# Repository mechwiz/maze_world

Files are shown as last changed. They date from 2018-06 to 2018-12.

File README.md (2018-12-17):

# Effect of Planning Depth in Predator-Prey Behavior
**Michael Wiznitzer**

Northwestern University: Final Project

## Introduction
Nature is a wonder of its own. When we look at animals, we usually see cute furry creatures that seemingly just do their own thing. After seeing them in the wild, though, you begin to notice how they use their environment to hunt or hide from other animals. For [example](https://youtu.be/LhSDxp0oQK8?t=2m51s), a leapord might hide in a narrow valley as it hunts imapla grazing above it. In order to better understand these predator-prey relationships, [research](https://nxr.northwestern.edu/planning-vertebrates) has been done in the NxR lab to simulate how prey will act (using POMDPs) given various planning depths in order to reach some goal position before a predator kills the prey. My project focuses on turning these simulations into a 3-D honeycomb-styled-world realization where Sphero robots act as the predator and prey that have to navigate in various levels of occluded environments.

####  Objective
The goal of this project is to demonstrate the effect of planning-depth in regards to prey being able to reach some goal position before the predator kills it in a 3-D honeycomb-styled-world environment with various levels of occlusion. This project breaks down into 3 different parts listed below:

- Maze Fabrication
- Sphero Control with ROS
- Image Processing to determine robot location in maze

To read more about each part, see my portfolio post [here](https://mechwiz.github.io/Portfolio/prey.html). This repo's purpose is to highlight all of the differenct modules designed and created for the **Maze Fabrication** part above. To read more about how to setup the sphero control package, see my other repo [here](https://github.com/mechwiz/maze_control).

## Maze Fabrication
There are two parts to designing the maze within which the 3-D simulations will occur. The obvious part is designing the full-scale maze which looks something like the picture below based on the specs described in my portfolio post.

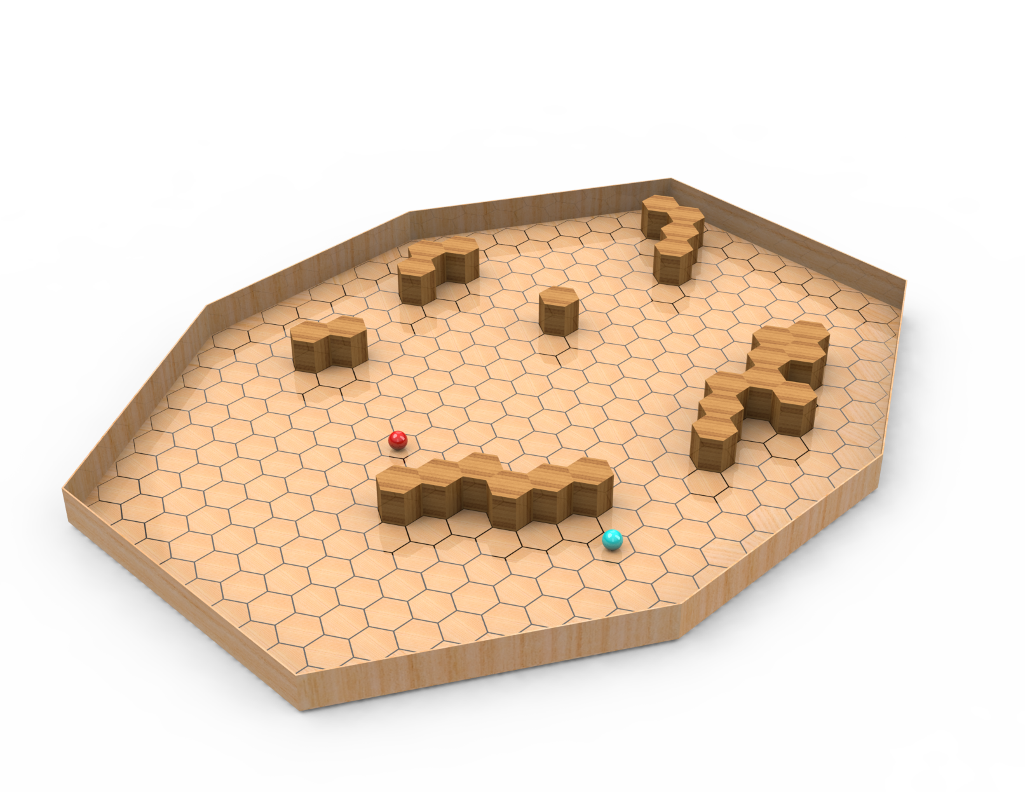
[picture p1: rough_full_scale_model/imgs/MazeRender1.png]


The full-scale maze includes 349 hexagonal cells and is roughly 8ft long by 6.25ft wide by 0.5ft tall. Due to the large size of the maze, the pieces are modular so that assembly and takedown is relatively straightforward.

Before building the full-scale maze, a small-scale version was made so that testing with the other parts of the project (i.e. controlling the Sphero robots with ROS via Image Processing) could be done. This way, if any modificaitons to the small scale maze had to be done in the interest of the other parts, they could be incorporated into the full-scale maze design. These changes are discussed in the **Full Scale Maze Design** section.

### Small Scale Maze Design
The small-scale maze design assembly model and actual laser-cut model are shown side by side below:

CAD Model                                                                          | Laser-cut Model
:---------------------------------------------------------------------------------:|:---------------------------------------------------------------------------------:
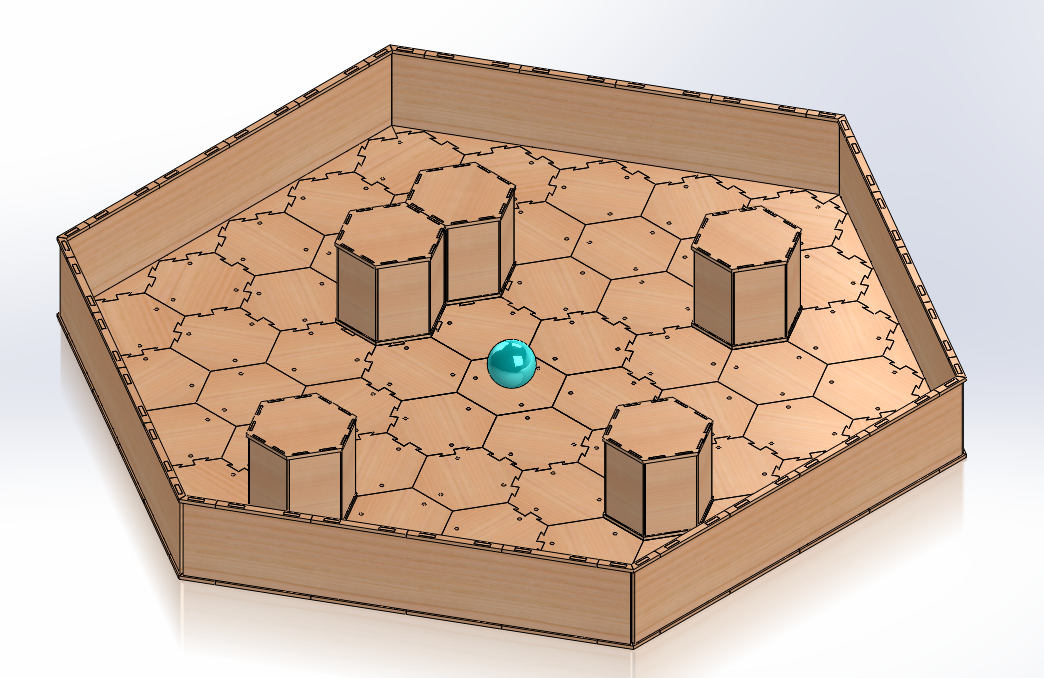
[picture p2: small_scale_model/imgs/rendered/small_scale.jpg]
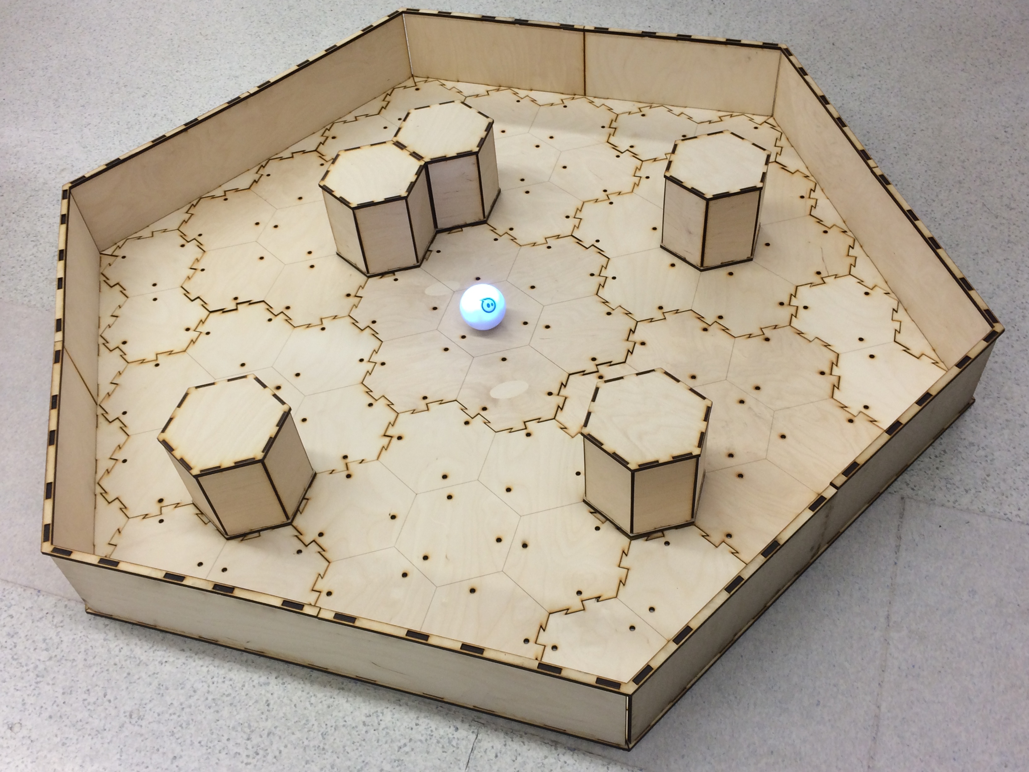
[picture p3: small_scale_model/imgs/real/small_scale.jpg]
 | 

The module pieces incorporated are described in the table below.

Description| CAD Model                                                                           | Laser-cut Model
:----------|:----------------------------------------------------------------------------------:|:----------------------------------------------------------------------------------:
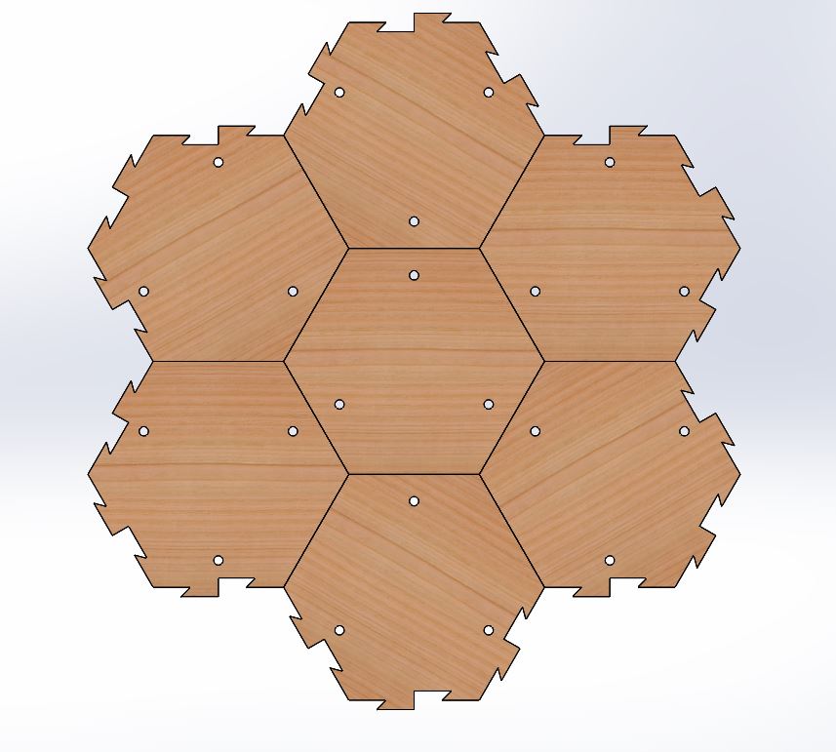
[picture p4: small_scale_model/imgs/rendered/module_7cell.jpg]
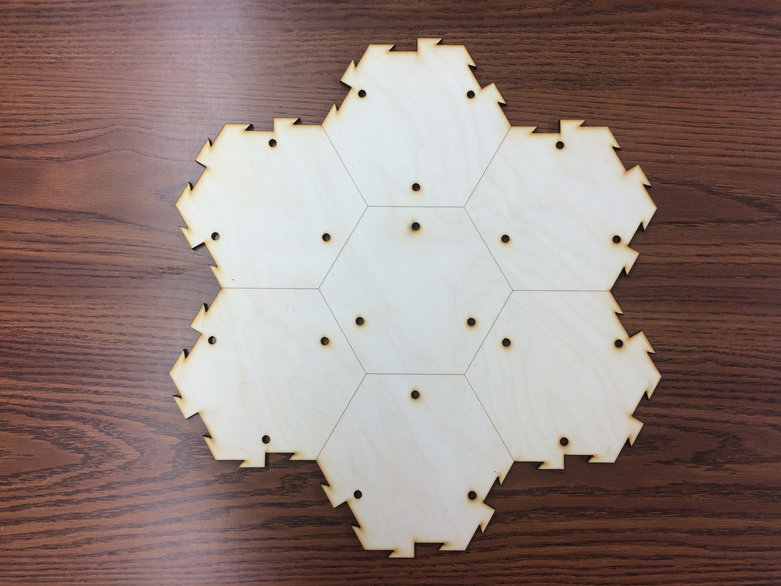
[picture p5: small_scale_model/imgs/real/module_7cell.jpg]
Modular interlocking floor piece with 7 cells <br /> (holes allow for obstacles to be "plugged" into the board via dowel pins) <ul><li>[DXF Files](small_scale_model/modules/module_7cell/dxf)</li><li>[SVG Files](small_scale_model/modules/module_7cell/svg)</li></ul> <br /> _7 modules_ |  | 
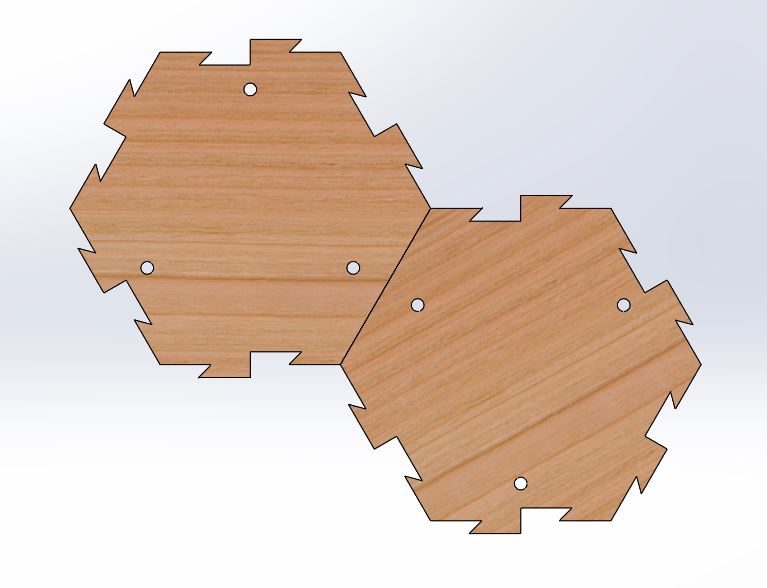
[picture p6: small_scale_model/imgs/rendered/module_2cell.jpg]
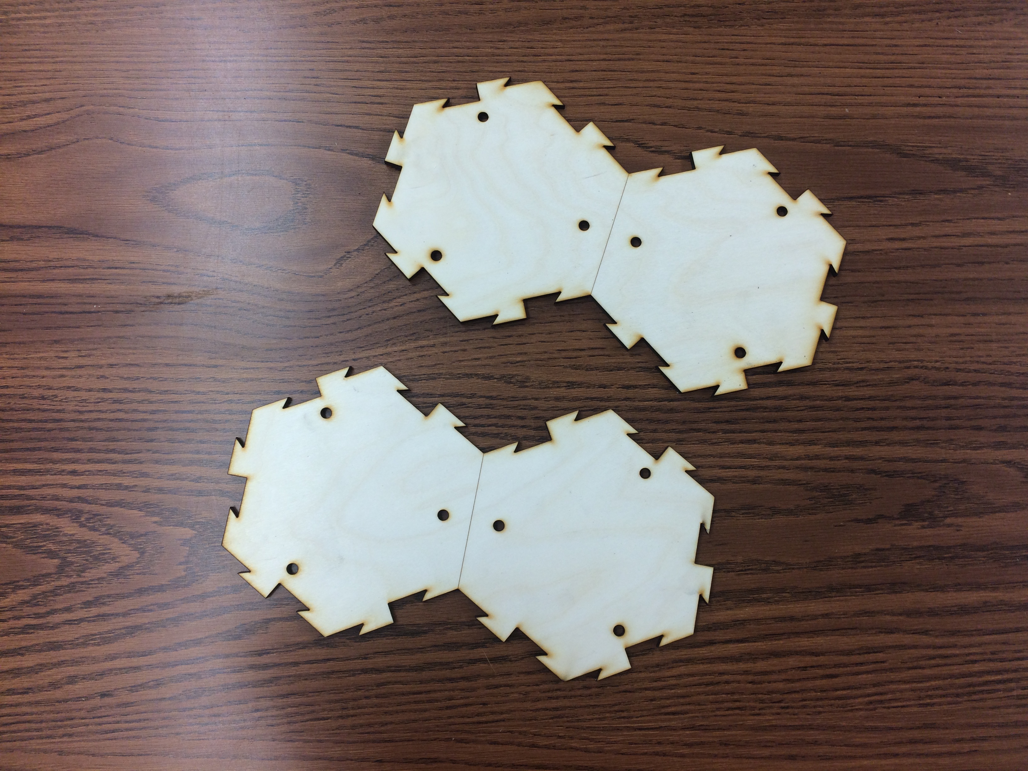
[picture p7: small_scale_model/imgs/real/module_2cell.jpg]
Modular interlocking floor piece with 2 cells <br /> (holes allow for obstacles to be "plugged" into the board via dowel pins) <ul><li>[DXF Files](small_scale_model/modules/module_2cell/dxf)</li><li>[SVG Files](small_scale_model/modules/module_2cell/svg)</li></ul> <br /> _4 modules_ |  | 
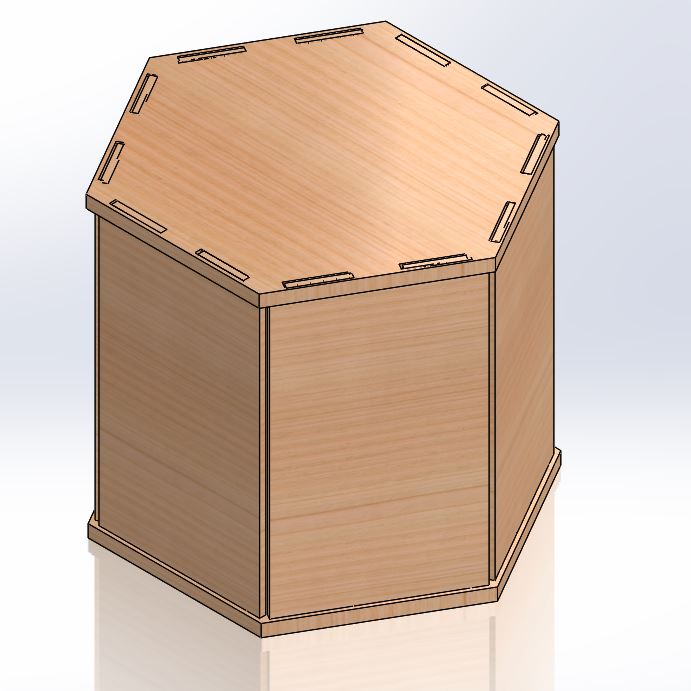
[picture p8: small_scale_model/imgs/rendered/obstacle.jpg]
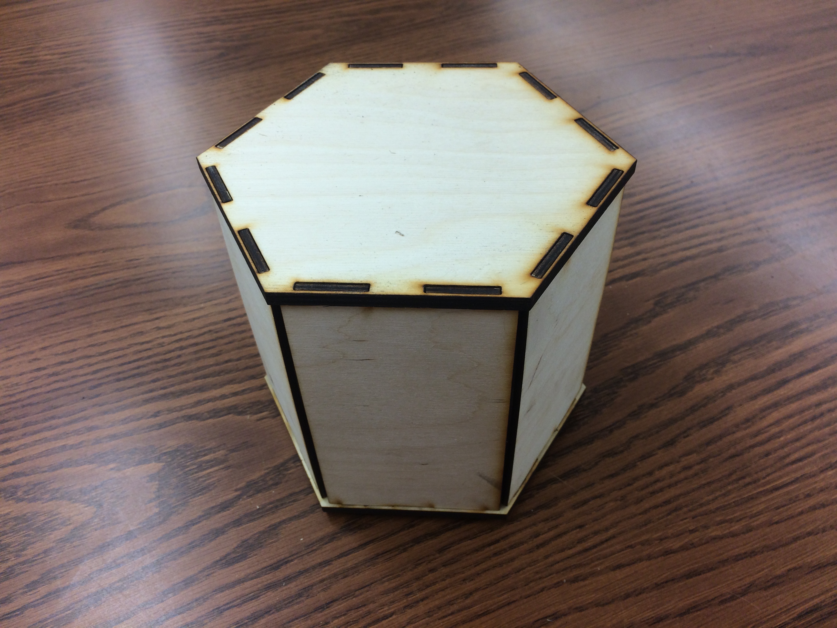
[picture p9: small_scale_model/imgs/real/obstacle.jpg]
Obstacle for blocking path of Sphero <br /> (uses a press-fit design; dowel pins glued <br /> on bottom are aligned with holes on the board) <ul><li>[DXF Files](small_scale_model/modules/obstacles/dxf)</li><li>[SVG Files](small_scale_model/modules/obstacles/svg)</li></ul> <br /> _Number of modules can vary_ |      | 
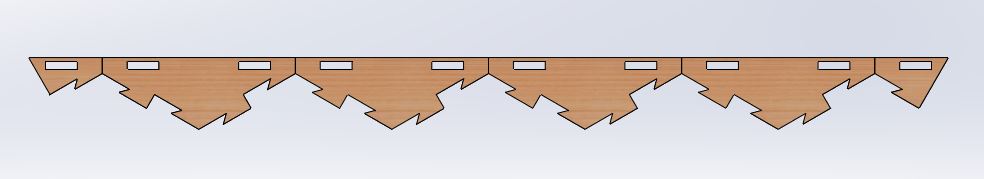
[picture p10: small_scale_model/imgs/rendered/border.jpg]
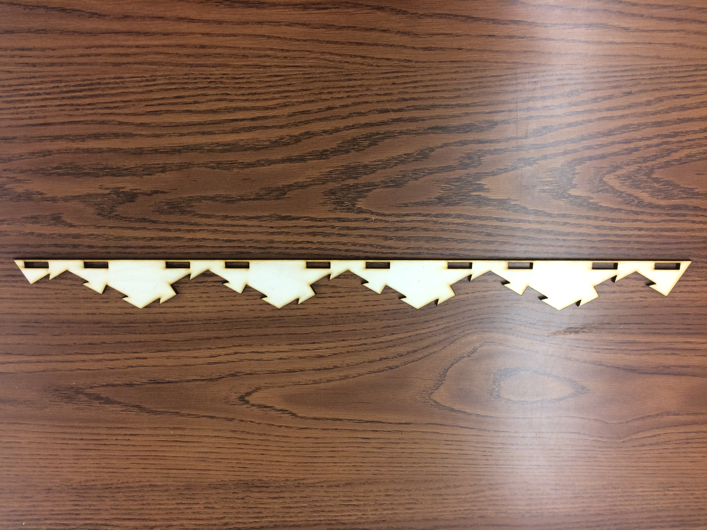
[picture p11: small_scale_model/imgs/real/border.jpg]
Interlocking border piece with the floor and wall pieces <ul><li>[DXF Files](small_scale_model/modules/border/dxf)</li><li>[SVG Files](small_scale_model/modules/border/svg)</li></ul> <br /> _6 modules_ |        | 
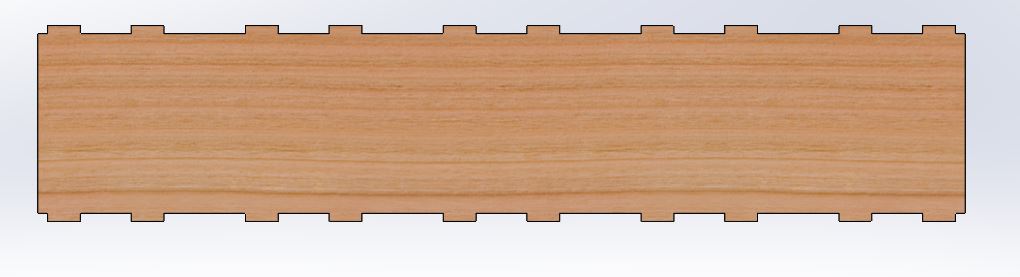
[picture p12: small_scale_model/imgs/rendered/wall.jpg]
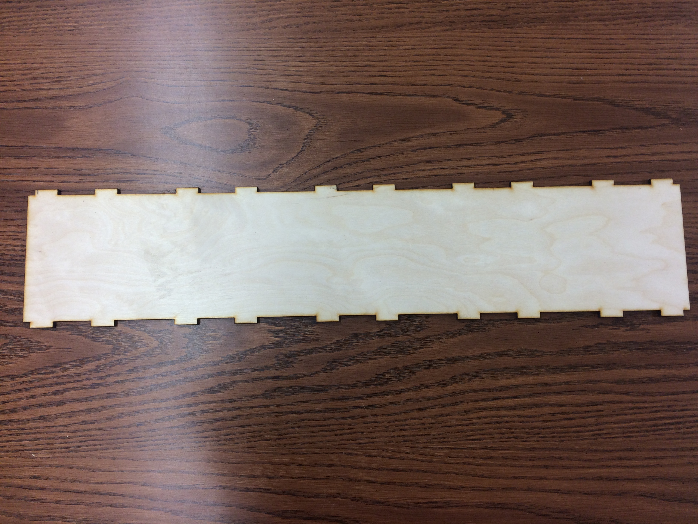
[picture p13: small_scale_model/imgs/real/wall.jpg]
Modular wall that fits into the border pieces <ul><li>[DXF Files](small_scale_model/modules/walls/dxf)</li><li>[SVG Files](small_scale_model/modules/walls/svg)</li></ul> <br /> _6 modules_ |          | 
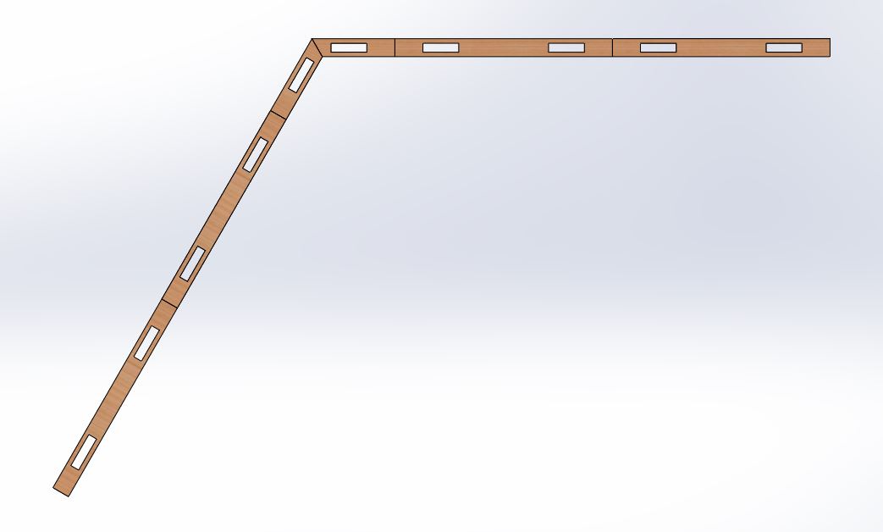
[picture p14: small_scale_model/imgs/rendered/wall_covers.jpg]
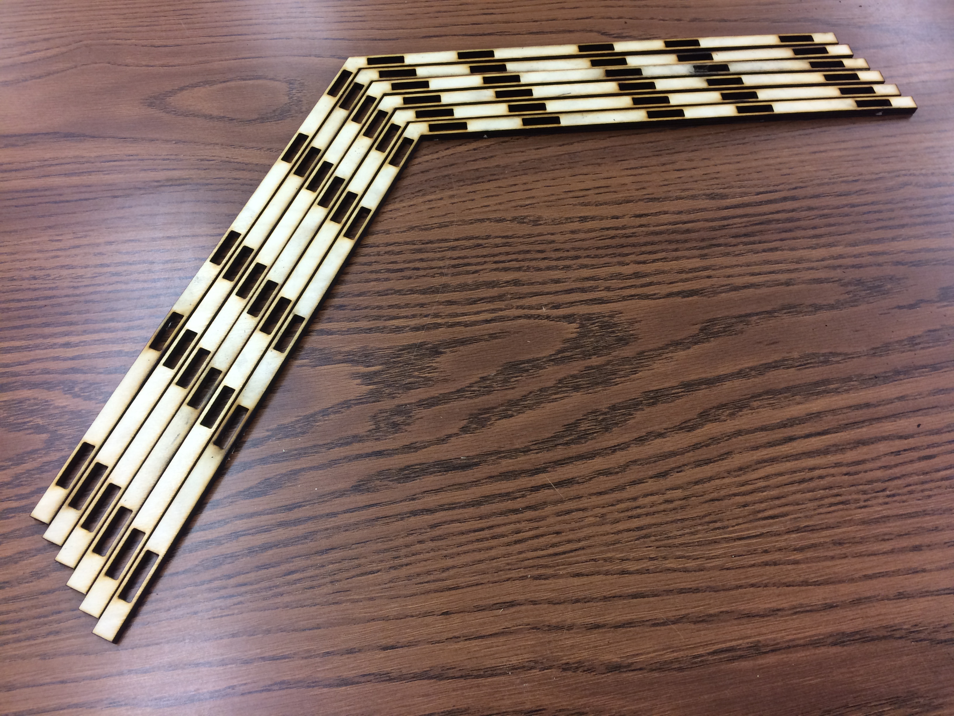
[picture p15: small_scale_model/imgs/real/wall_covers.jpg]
Modular wall cover that secures the wall pieces together <ul><li>[DXF Files](small_scale_model/modules/wall_covers/dxf)</li><li>[SVG Files](small_scale_model/modules/wall_covers/svg)</li></ul> <br /> _6 modules_ |   | 

### Full Scale Maze Design
The current full-scale maze design assembly model is shown below. Some modifications were made based on testing in the small-scale maze and due to size restrictions. There was no space available that could fit the maze with its original dimensions (11ft long by 8.6ft wide) so the cell size was reduced (where each side of the hexagon was changed from 3.5in to 2.5in) in order to maintain the same number of cells as required by spec. As such, the Sphero 2.0 was no longer an option as its diameter is roughly 3 inches. The Sphero Mini was chosen instead as its diameter is a little under 2 inches. Hence all full-scale module pieces were modified to reflect this change. The other change that will be implemented based on testing in the small-scale and full-scale mazes is that a [clear vinyl mat](https://www.marinevinylfabric.com/products/clear-marine-vinyl?variant=14023793573972) will be spread out over the surface of the maze. This is because some of the wood pieces are slightly warped which makes some catch points near the module connections that could potentially inhibit movement of the Sphero Mini (something that wasn't an issue for the Sphero 2.0). The mat will help make a continous smooth surface that the Sphero Mini will be able to move on with no issue. It should also be noted that holes will be punched on the mat corresponding to the hole places on the wood surface of the maze. These holes will not inhibit the Sphero movement as the mat is very thin (around 0.4 mm). Also note that because each cell of the maze will be labeled using a labeling scheme, the holes will always line up with those on the mat.

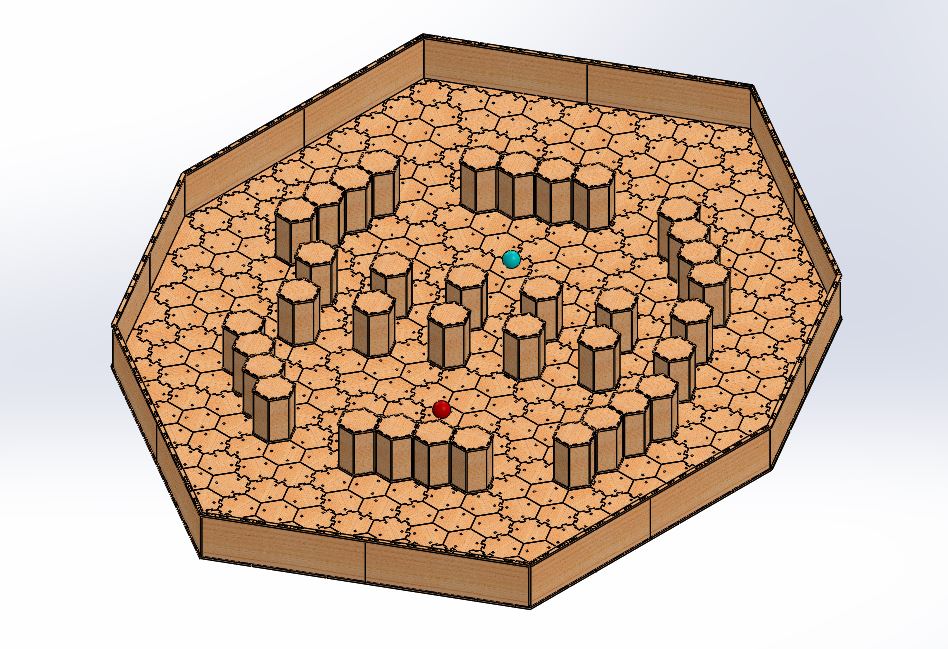
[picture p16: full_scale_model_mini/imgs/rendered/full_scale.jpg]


The module pieces incorporated are described in the table below.

Description| CAD Model                                                                           | Laser-cut Model
:----------|:----------------------------------------------------------------------------------:|:----------------------------------------------------------------------------------:
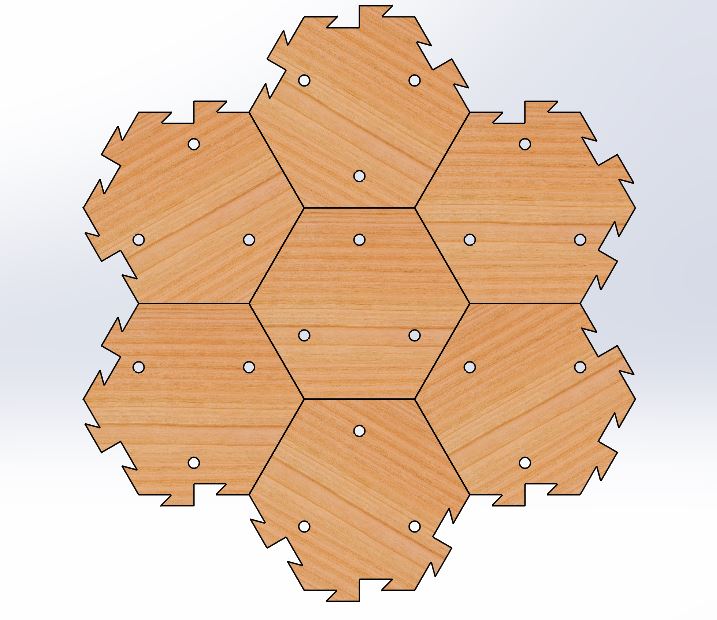
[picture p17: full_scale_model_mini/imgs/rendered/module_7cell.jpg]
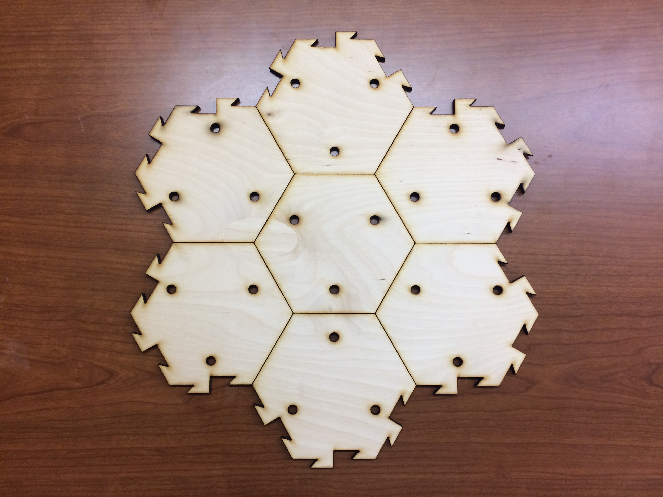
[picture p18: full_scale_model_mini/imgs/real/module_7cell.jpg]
Modular interlocking floor piece with 7 cells <br /> (holes allow for obstacles to be "plugged" into the board via dowel pins) <ul><li>[DXF Files](full_scale_model_mini/modules/module_7cell/dxf)</li><li>[SVG Files](full_scale_model_mini/modules/module_7cell/svg)</li></ul> <br /> _41 modules_ |  | 
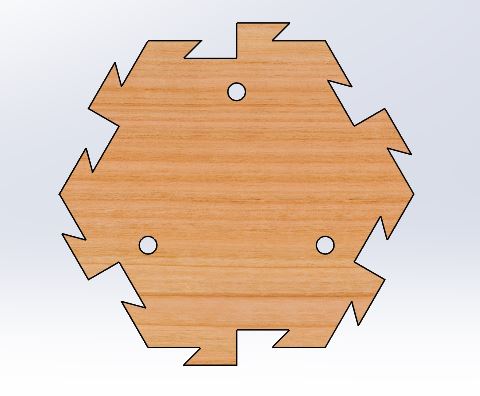
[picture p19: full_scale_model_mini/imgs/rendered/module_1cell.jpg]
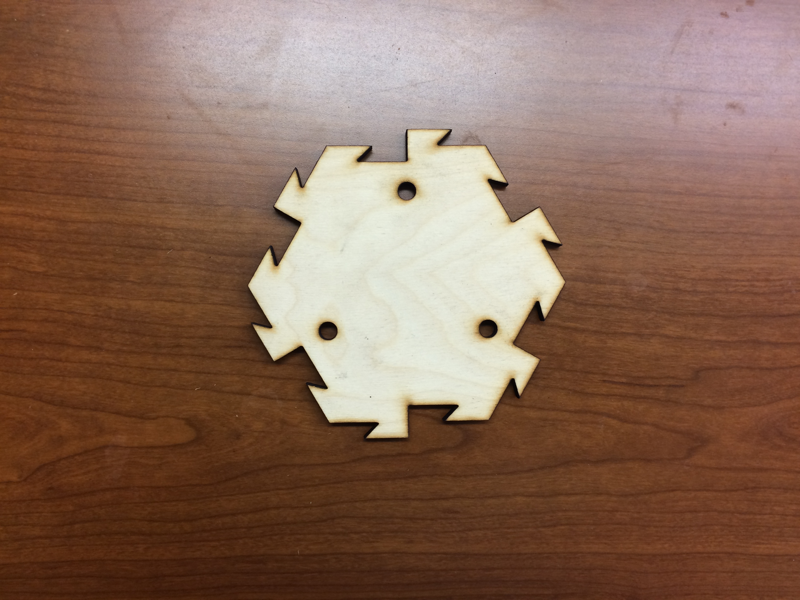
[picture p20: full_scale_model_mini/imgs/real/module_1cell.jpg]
Modular interlocking floor piece with 1 cell <br /> (holes allow for obstacles to be "plugged" into the board via dowel pins) <ul><li>[DXF Files](full_scale_model_mini/modules/module_1cell/dxf)</li><li>[SVG Files](full_scale_model_mini/modules/module_1cell/svg)</li></ul> <br /> _6 modules_ |  | 
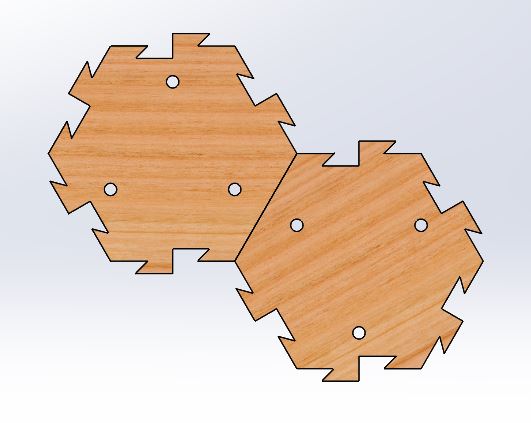
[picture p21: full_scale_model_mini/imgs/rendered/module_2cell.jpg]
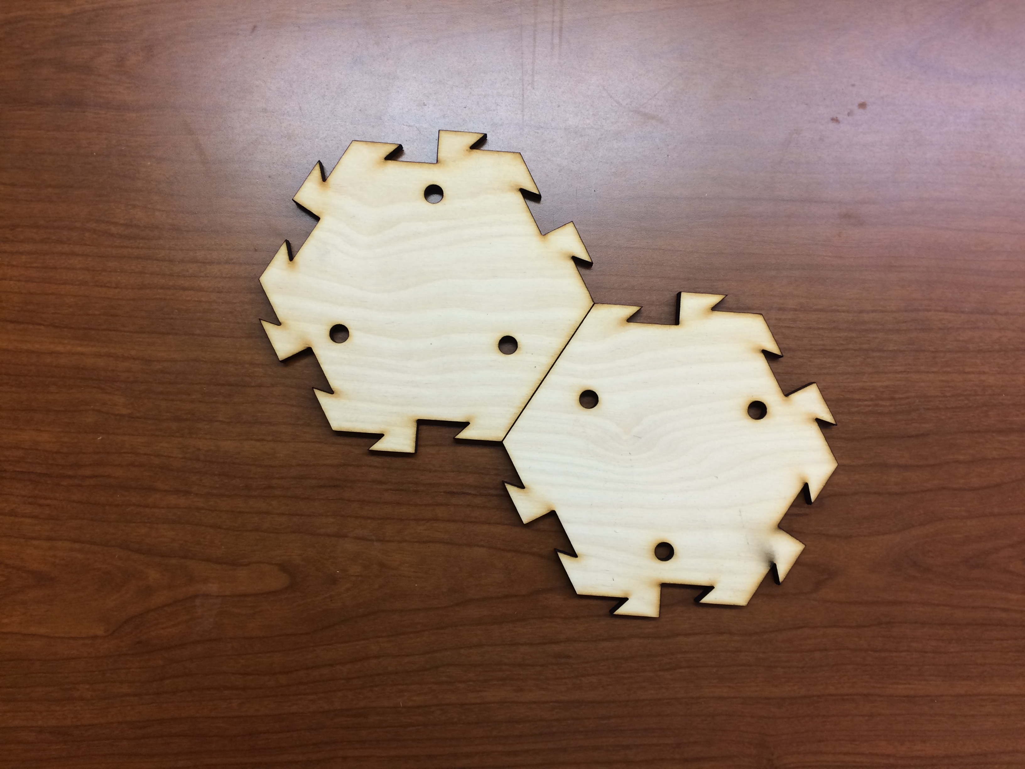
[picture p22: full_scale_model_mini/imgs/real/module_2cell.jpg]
Modular interlocking floor piece with 2 cells <br /> (holes allow for obstacles to be "plugged" into the board via dowel pins) <ul><li>[DXF Files](full_scale_model_mini/modules/module_2cell/dxf)</li><li>[SVG Files](full_scale_model_mini/modules/module_2cell/svg)</li></ul> <br /> _2 modules_ |  | 
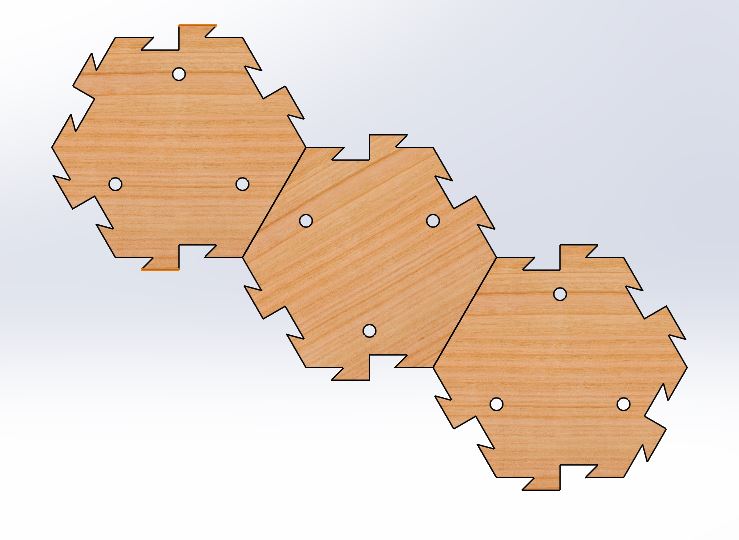
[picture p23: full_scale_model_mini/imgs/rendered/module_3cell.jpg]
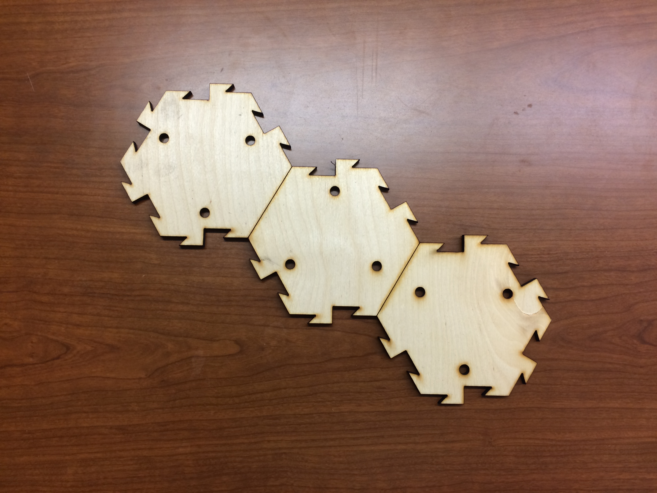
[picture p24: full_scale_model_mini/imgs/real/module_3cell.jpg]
Modular interlocking floor piece with 3 cells <br /> (holes allow for obstacles to be "plugged" into the board via dowel pins) <ul><li>[DXF Files](full_scale_model_mini/modules/module_3cell/dxf)</li><li>[SVG Files](full_scale_model_mini/modules/module_3cell/svg)</li></ul> <br /> _4 modules_ |  | 
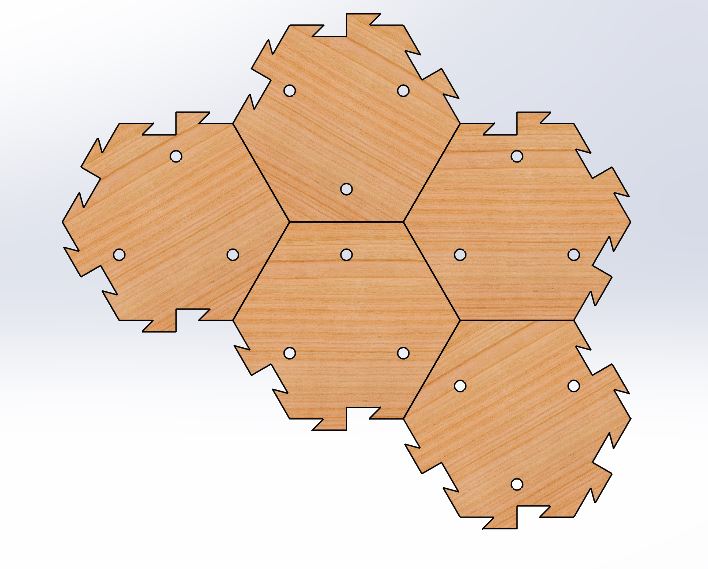
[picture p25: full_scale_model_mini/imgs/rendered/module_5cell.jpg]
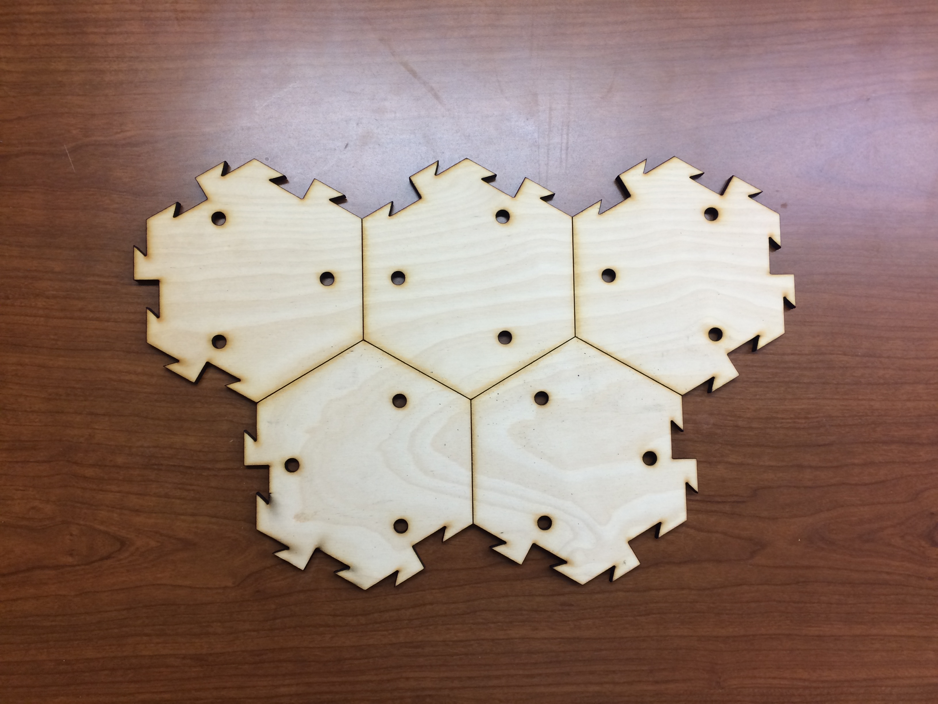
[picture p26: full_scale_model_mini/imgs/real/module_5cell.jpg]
Modular interlocking floor piece with 5 cells <br /> (holes allow for obstacles to be "plugged" into the board via dowel pins) <ul><li>[DXF Files](full_scale_model_mini/modules/module_5cell/dxf)</li><li>[SVG Files](full_scale_model_mini/modules/module_5cell/svg)</li></ul> <br /> _8 modules_ |  | 
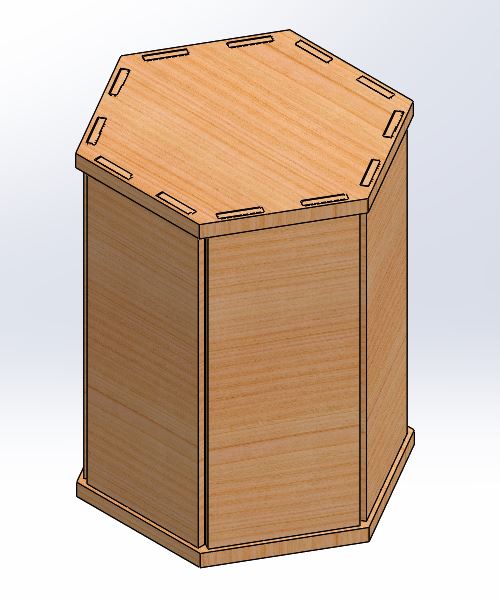
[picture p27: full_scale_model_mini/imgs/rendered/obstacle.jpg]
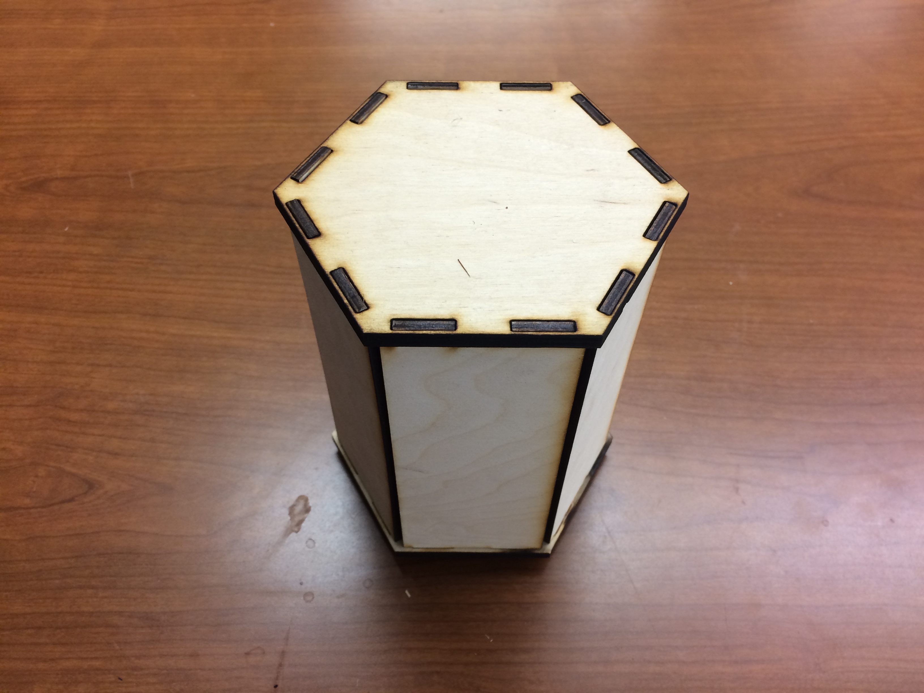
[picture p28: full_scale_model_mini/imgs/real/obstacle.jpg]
Obstacle for blocking path of Sphero <br /> (uses a press-fit design; dowel pins glued <br /> on bottom are aligned with holes on the board) <ul><li>[DXF Files](full_scale_model_mini/modules/obstacles/dxf)</li><li>[SVG Files](full_scale_model_mini/modules/obstacles/svg)</li></ul> <br /> _Number of modules can vary_ |      | 
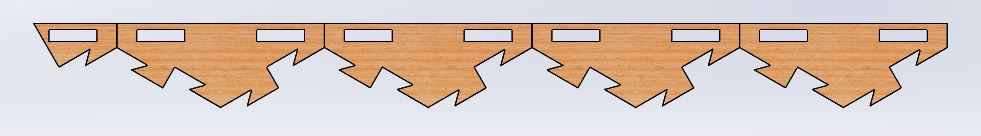
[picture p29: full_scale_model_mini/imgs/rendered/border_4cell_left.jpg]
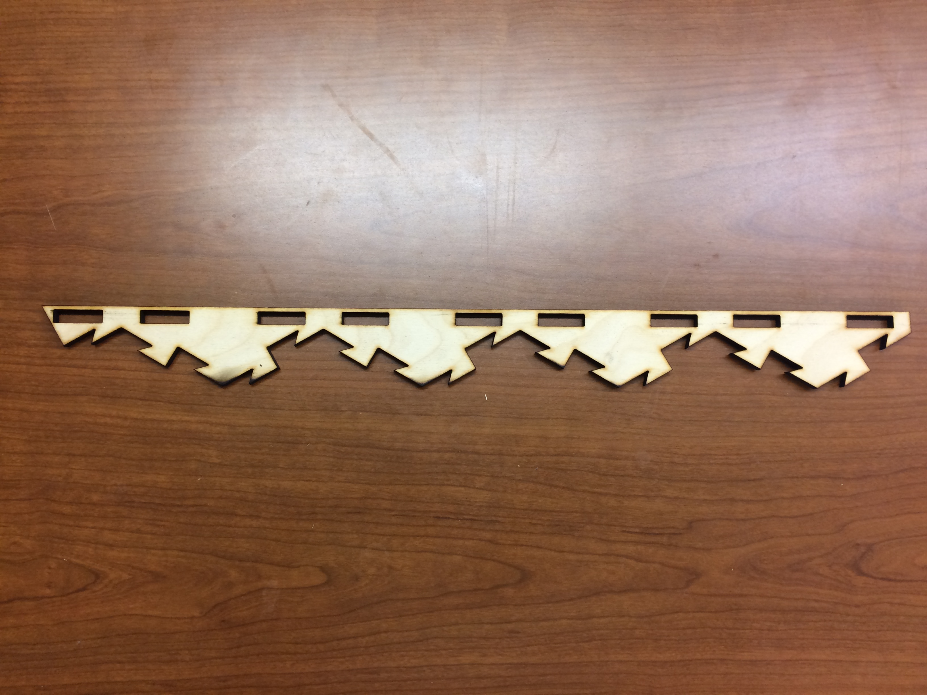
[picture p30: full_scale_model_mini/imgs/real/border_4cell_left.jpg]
Interlocking border piece with the floor and wall pieces <ul><li>[DXF Files](full_scale_model_mini/modules/border_4cell_left/dxf)</li><li>[SVG Files](full_scale_model_mini/modules/border_4cell_left/svg)</li></ul> <br /> _6 modules_ |  | 
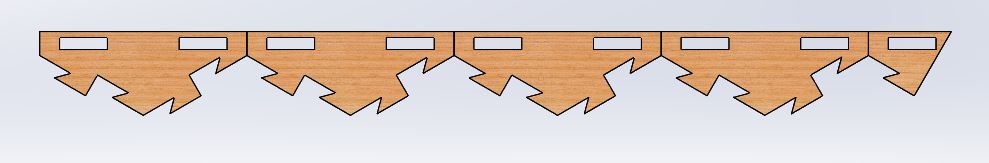
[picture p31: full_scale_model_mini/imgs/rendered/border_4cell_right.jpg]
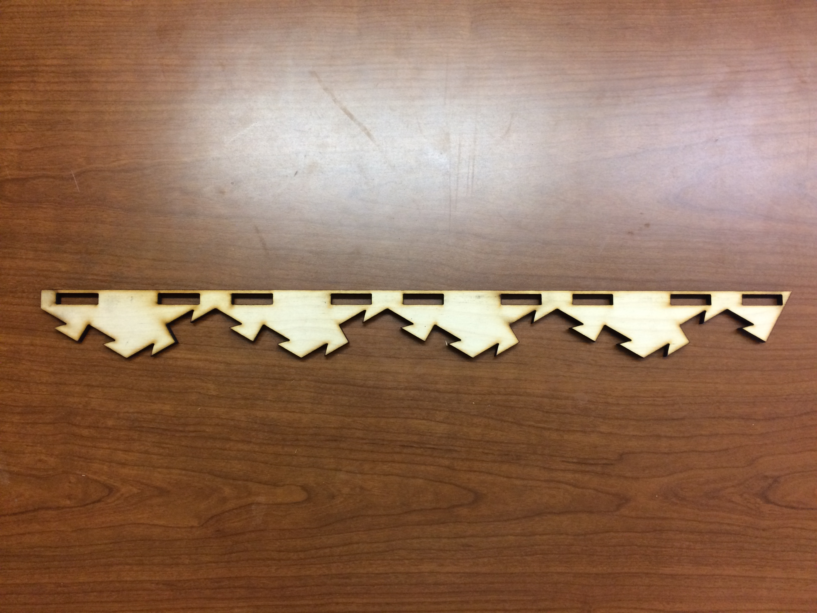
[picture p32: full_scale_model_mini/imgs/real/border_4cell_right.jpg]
Interlocking border piece with the floor and wall pieces <ul><li>[DXF Files](full_scale_model_mini/modules/border_4cell_right/dxf)</li><li>[SVG Files](full_scale_model_mini/modules/border_4cell_right/svg)</li></ul> <br /> _6 modules_ |  | 
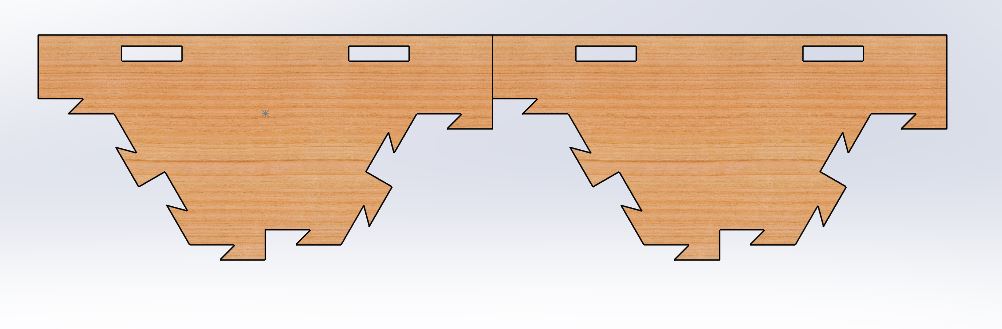
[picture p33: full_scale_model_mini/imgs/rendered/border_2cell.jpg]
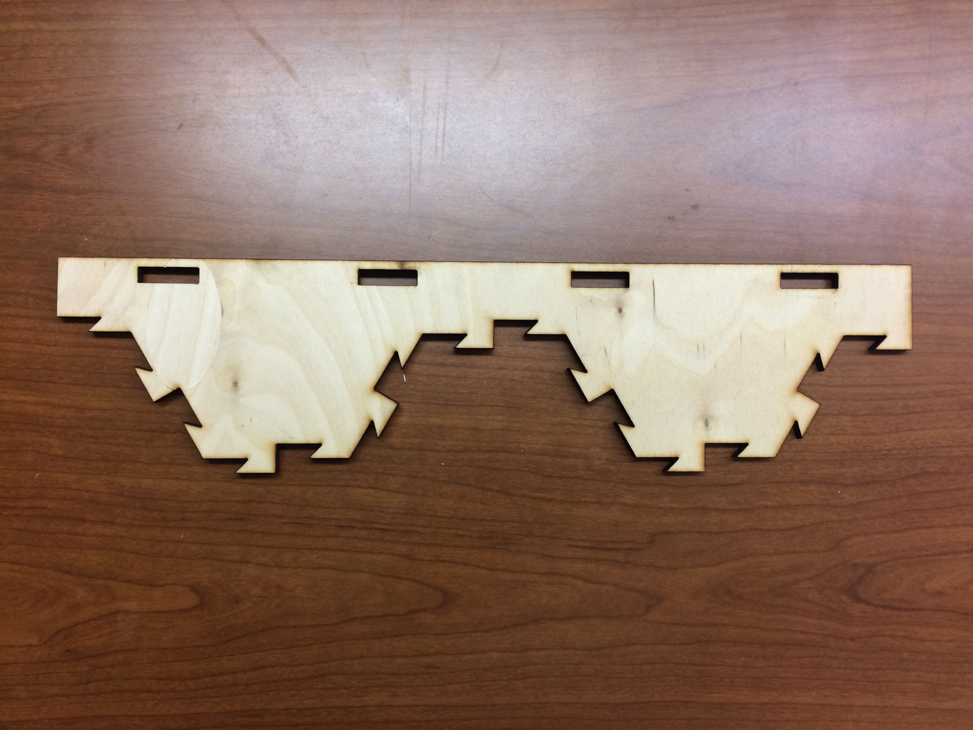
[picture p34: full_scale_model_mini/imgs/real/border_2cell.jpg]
Interlocking border piece with the floor and wall pieces <ul><li>[DXF Files](full_scale_model_mini/modules/border_2cell/dxf)</li><li>[SVG Files](full_scale_model_mini/modules/border_2cell/svg)</li></ul> <br /> _4 modules_ |  | 
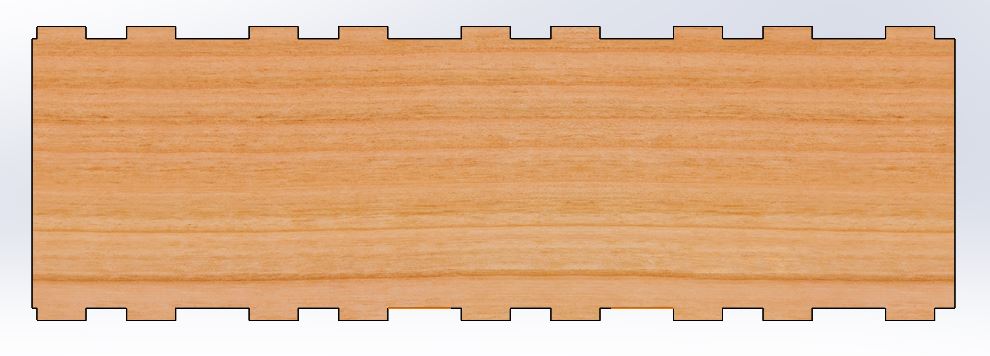
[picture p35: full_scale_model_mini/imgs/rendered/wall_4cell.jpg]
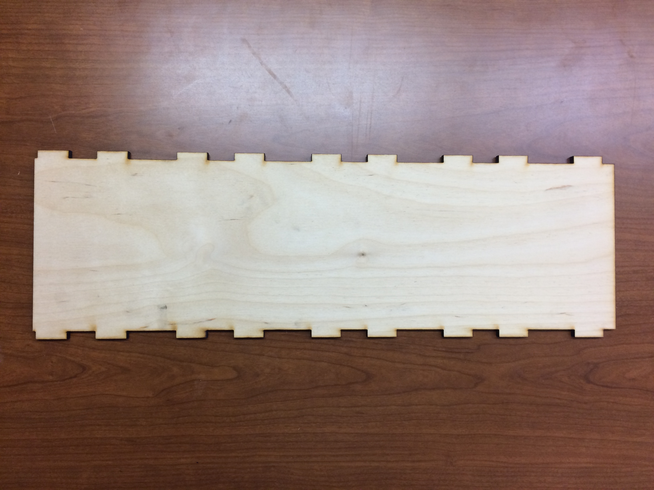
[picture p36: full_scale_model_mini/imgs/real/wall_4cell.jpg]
Modular wall that fits into the border pieces <ul><li>[DXF Files](full_scale_model_mini/modules/wall_4cell/dxf)</li><li>[SVG Files](full_scale_model_mini/modules/wall_4cell/svg)</li></ul> <br /> _12 modules_ |          | 
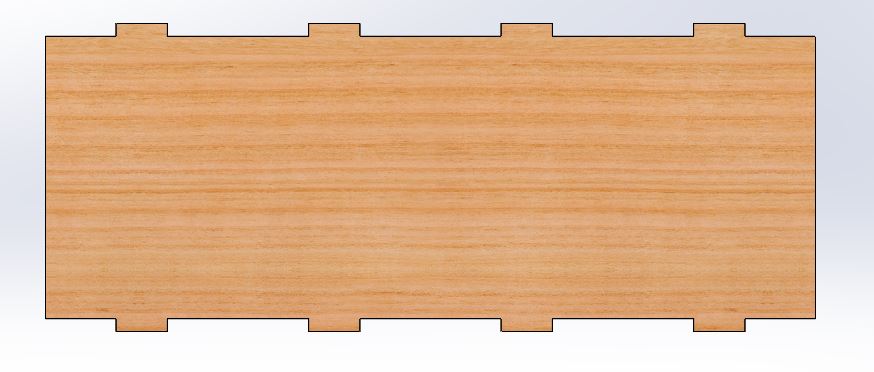
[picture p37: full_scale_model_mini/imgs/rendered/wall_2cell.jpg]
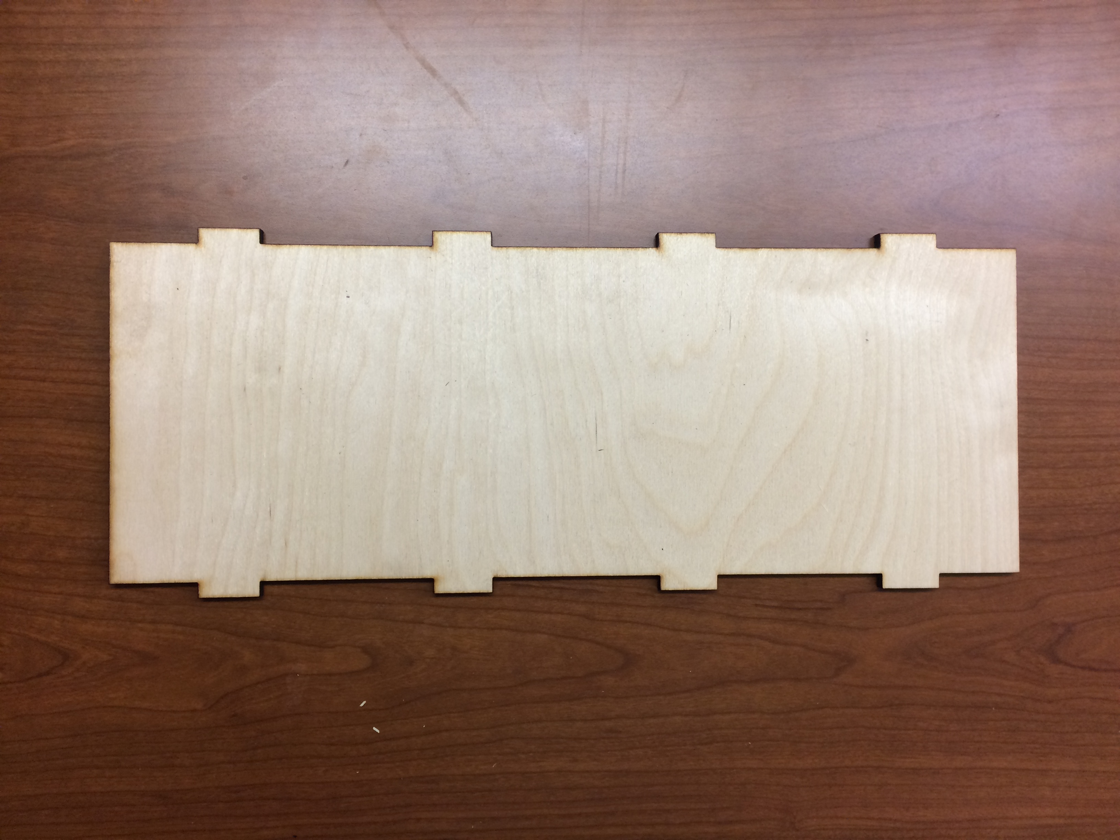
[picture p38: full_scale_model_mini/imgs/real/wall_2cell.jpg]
Modular wall that fits into the border pieces <ul><li>[DXF Files](full_scale_model_mini/modules/wall_2cell/dxf)</li><li>[SVG Files](full_scale_model_mini/modules/wall_2cell/svg)</li></ul> <br /> _4 modules_ |          | 
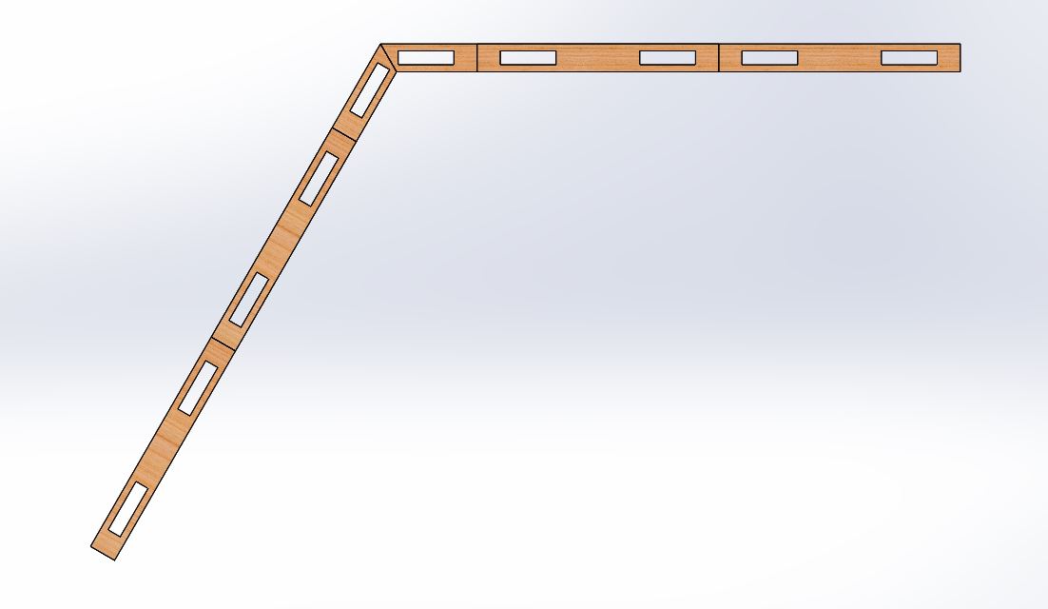
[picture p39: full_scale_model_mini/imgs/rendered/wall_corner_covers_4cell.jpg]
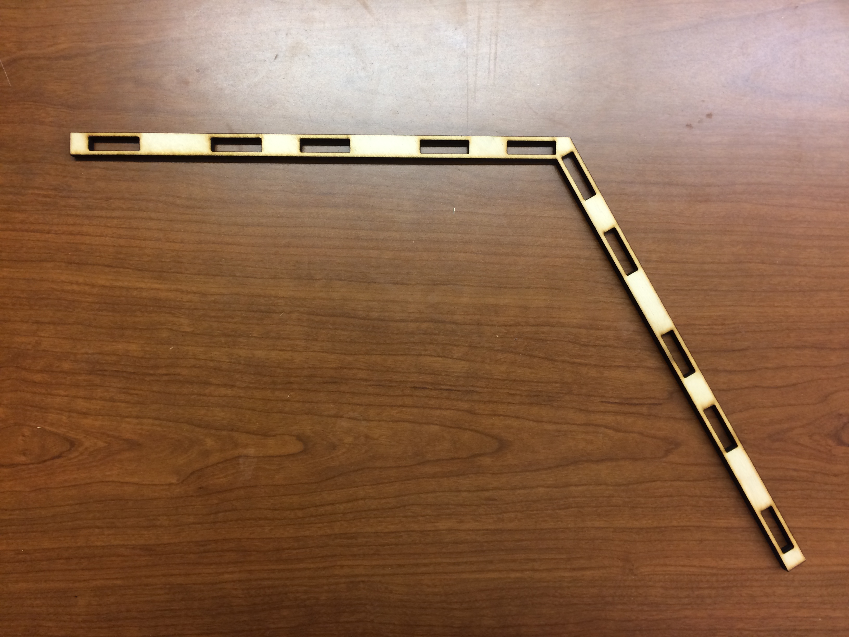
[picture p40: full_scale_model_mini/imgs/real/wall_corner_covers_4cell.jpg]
Modular wall cover that secures the wall pieces together <ul><li>[DXF Files](full_scale_model_mini/modules/wall_corner_covers_4cell/dxf)</li><li>[SVG Files](full_scale_model_mini/modules/wall_corner_covers_4cell/svg)</li></ul> <br /> _4 modules_ |   | 
Modular wall cover that secures the wall pieces together <ul><li>[DXF Files](full_scale_model_mini/modules/wall_corner_covers_2cell/dxf)</li><li>[SVG Files](full_scale_model_mini/modules/wall_corner_covers_2cell/svg)</li></ul> <br /> _4 modules_ |   | 
Modular wall cover that secures the wall pieces together <ul><li>[DXF Files](full_scale_model_mini/modules/wall_middle_covers_4cell/dxf)</li><li>[SVG Files](full_scale_model_mini/modules/wall_middle_covers_4cell/svg)</li></ul> <br /> _6 modules_ |   | 
Modular wall cover that secures the wall pieces together <ul><li>[DXF Files](full_scale_model_mini/modules/wall_middle_covers_2cell/dxf)</li><li>[SVG Files](full_scale_model_mini/modules/wall_middle_covers_2cell/svg)</li></ul> <br /> _2 modules_ |   | 

### Part Modifications
An ultimate goal of the project is to have a mouse be chased around by a Sphero and to analyze the path that the mouse takes so that our predator-prey path models can be verified and/or updated. Since mice can jump fairly high (even higher than the current 0.5ft height of the maze), a plexiglass cover (such as 2 pieces of [this](https://www.homedepot.com/p/OPTIX-48-in-x-96-in-x-1-8-in-Clear-Acrylic-Sheet-MC-100S/205351353) along the length of the maze) can be set over the maze to prevent any mice from jumping over obstacles and walls. The cover can be supported by the walls of the maze and any obstacles within. In the event that this affects how the mice will plan, an alternative approach (though much more involving) is to make modifications to the wall components within the maze as described in the following procedure:

1. Open up the following part files in Solidworks:
  - [wall_2cell](full_scale_model_mini/modules/wall_2cell/wall_2cell_mult.SLDPRT)
  - [wall_4cell](full_scale_model_mini/modules/wall_4cell/wall_4cell_mult.SLDPRT)
  - [obstacle_wall_mult](full_scale_model_mini/modules/obstacles/obstacle_wall_mult.SLDPRT)
2. Change the height dimension in their corresponding sketches from 6 inches to however many inches are desired
3. Save the files as dxf files (from the top plane)
4. Import these files into Inkscape, and save them as svg files
5. Using a laser cutter, cut out the newly updated walls
  - For the **wall_2cell** and **wall_4cell** walls, use [1/4 inch 20"x30" birch plywood](https://www.woodworkerssource.com/shop/product/14balpack3.html)
  - For the **obstacle_wall** walls, use [1/8 inch 20"x30" birch plywood](https://www.woodworkerssource.com/shop/product/18balpack3.html)
6. Replace the shorter walls with the taller walls
  - Just a fair warning, this may be tedious work when it comes to the obstacles. You will first need to remove the current walls using a flat-head screwdriver as a lever since the obstacles have a press-fit design. You will then need to install the new walls as described in the obstacle building manual [here](obstacle_procedure.md). This manual is also helpful in case more obstacles need to be built.

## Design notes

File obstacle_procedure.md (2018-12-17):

# Effect of Planning Depth in Predator-Prey Behavior
**Michael Wiznitzer**

Northwestern University: Final Project

## Obstacle Building Procedure

#### Obstacle Parts
Each obstacle consists of the following parts:
- [Obstacle Base](full_scale_model_mini/modules/obstacles/svg/obstacle_base.svg)
- [Obstacle Cover](full_scale_model_mini/modules/obstacles/svg/obstacle_cover.svg)
- [Obstacle Securing Piece](full_scale_model_mini/modules/obstacles/svg/obstacle_secure.svg)
- 6 [Obstacle Walls](full_scale_model_mini/modules/obstacles/svg/obstacle_wall.svg)
- 3 [dowel pins](https://www.mcmaster.com/90145a537)

If you would like to cut out multiple parts at one time, you can use the svg files where "\_mult" is added on to the file name. The rule of thumb for laser-cutting these files is to cut out the blue-lines on the first pass, and the black lines on the next pass.

#### Obstacle Building Procedure
1. Take an obstacle base and lay it down so that the nice side is touching the table. Then add some wood glue as shown below.

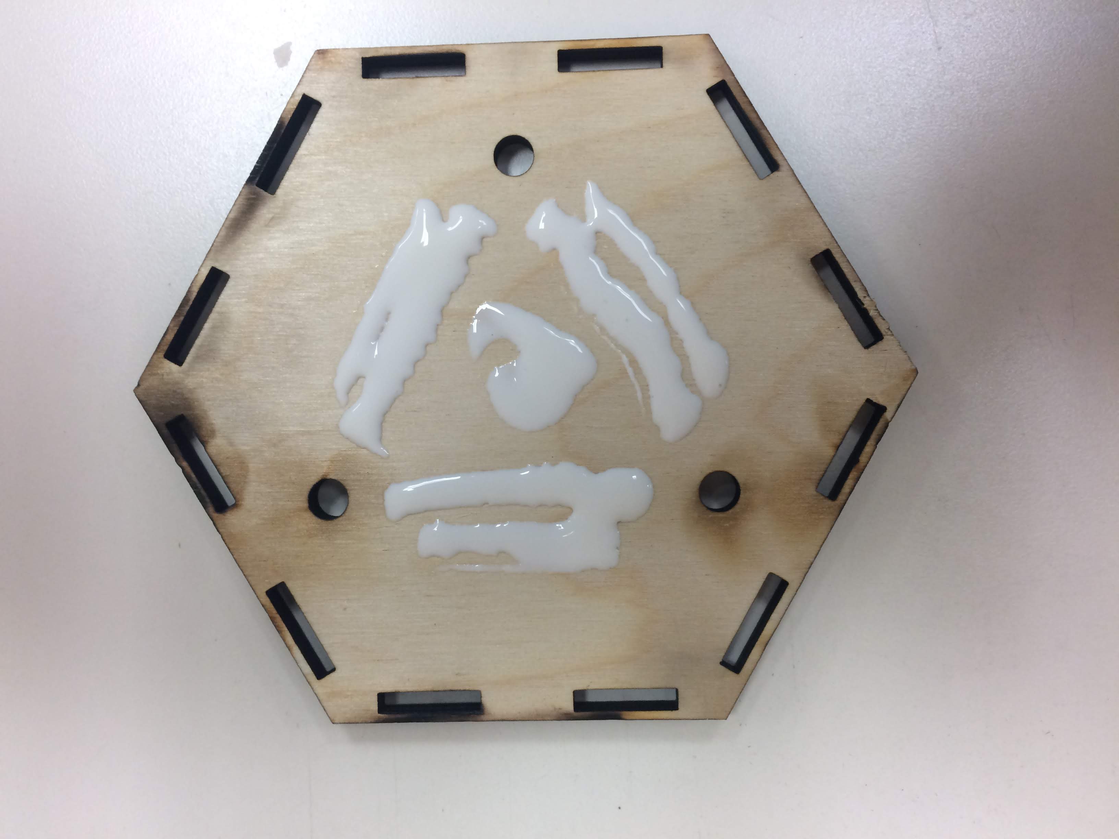
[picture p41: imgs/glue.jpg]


2. Take an obstacle securing piece and place it on the glue as shown. Press down firmly on it.

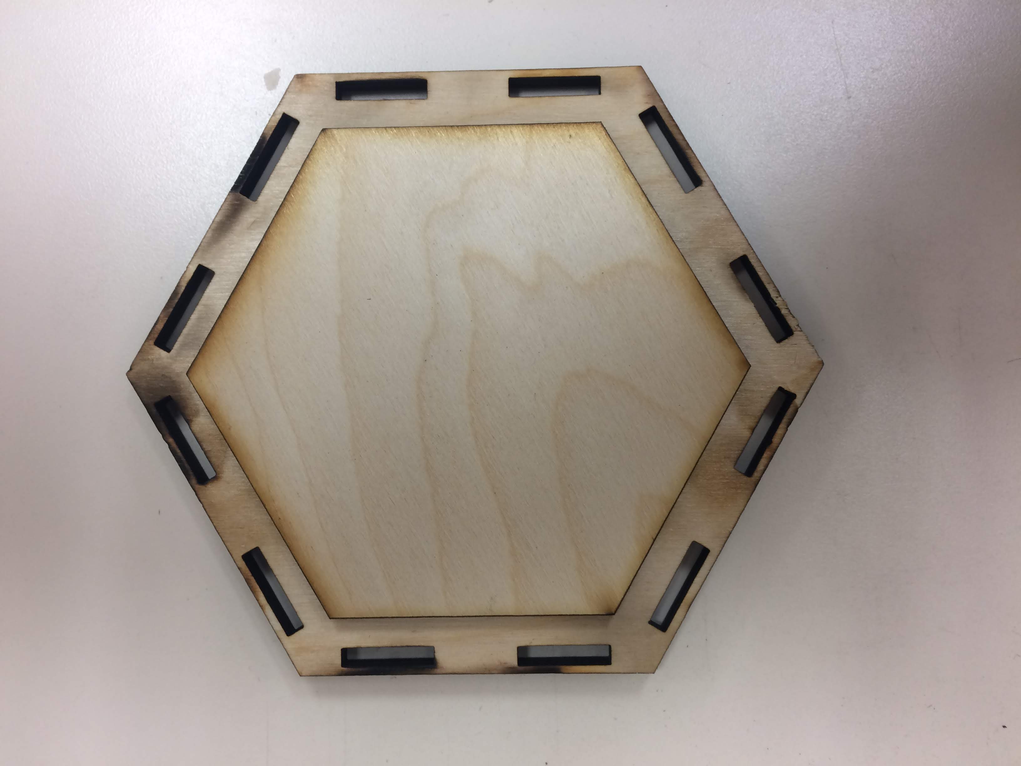
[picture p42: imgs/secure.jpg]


3. Flip the glued obstacle base over.

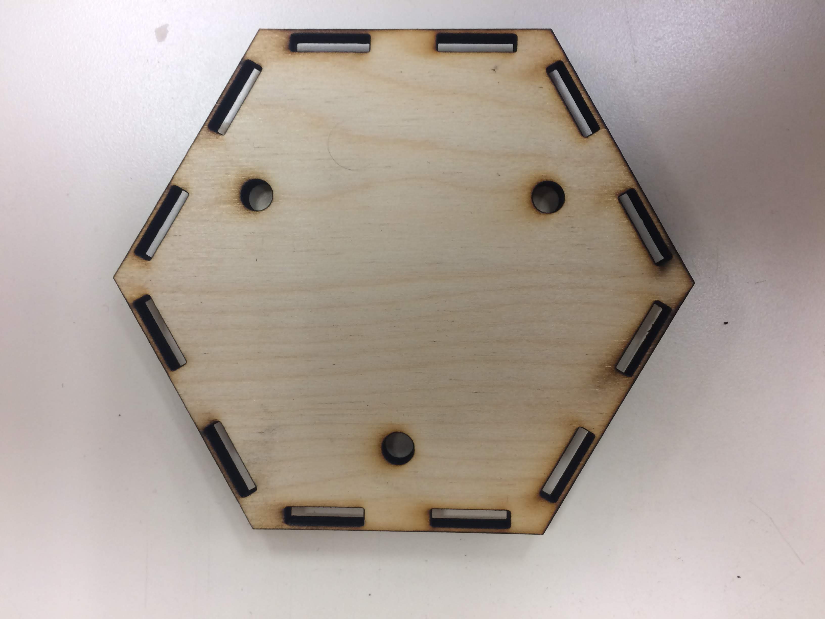
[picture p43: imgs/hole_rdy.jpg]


4. Put a drop of glue into each of the holes

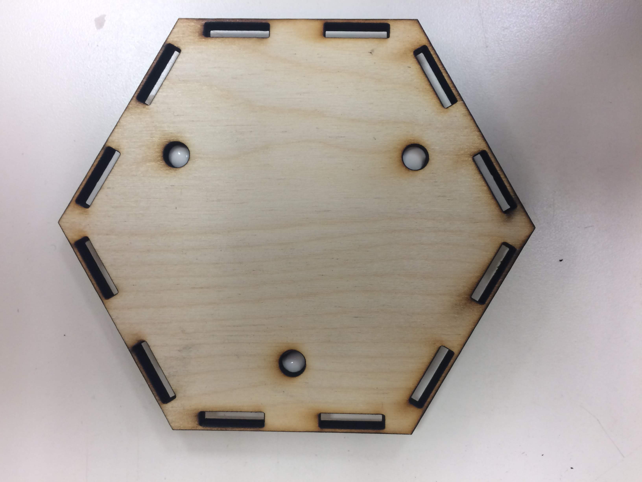
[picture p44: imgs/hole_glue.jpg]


5. Place 1 dowel pin firmly into each of the holes and wipe any glue that spills out of the hole

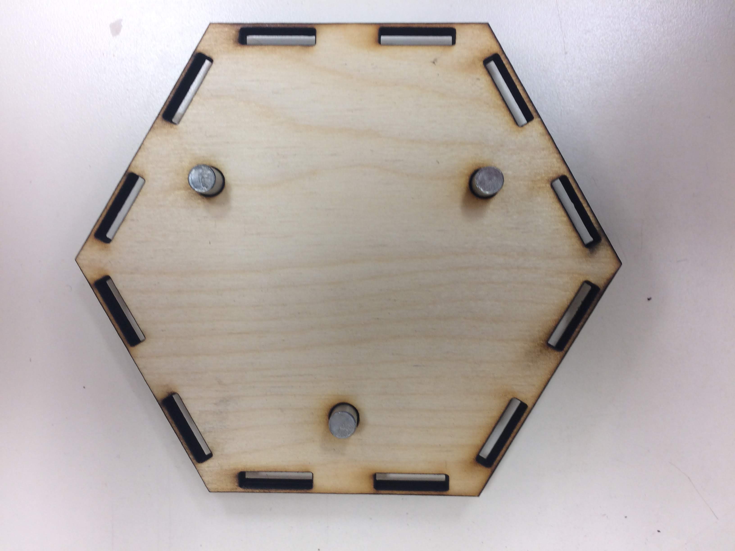
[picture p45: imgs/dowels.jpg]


6. Place the obstacle base onto an upside down 7-cell modular piece to dry as shown. Wipe any glue that formed around the lip of the securing piece.

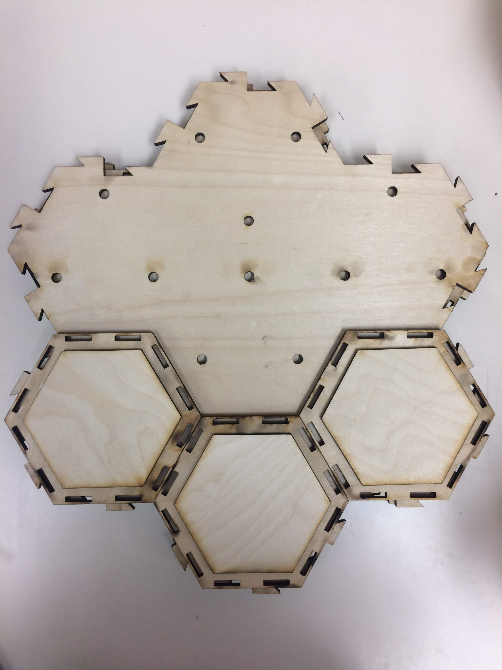
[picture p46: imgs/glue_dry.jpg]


7. Depending on how many obstacles you are making, fill the 7-cell modular piece to its capacity. Then place some heavy books on it so that the glue can dry on the pieces while they are being pressed together. Wait for an hour or two.

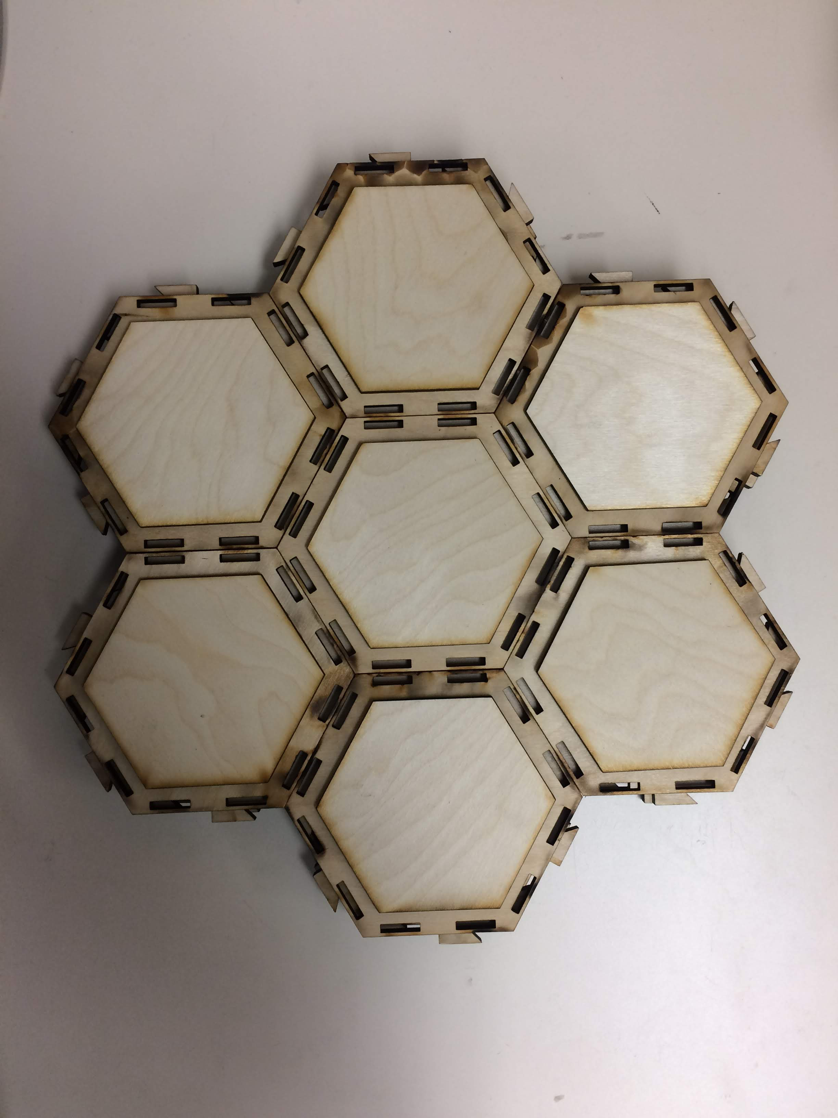
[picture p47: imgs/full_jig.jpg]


8. Take an obstacle cover and flip it so that the nice side is touching the table. Place walls into each of the 6 spots on the cover as shown. Make sure the nice sides are facing towards the outside of the obstacle.

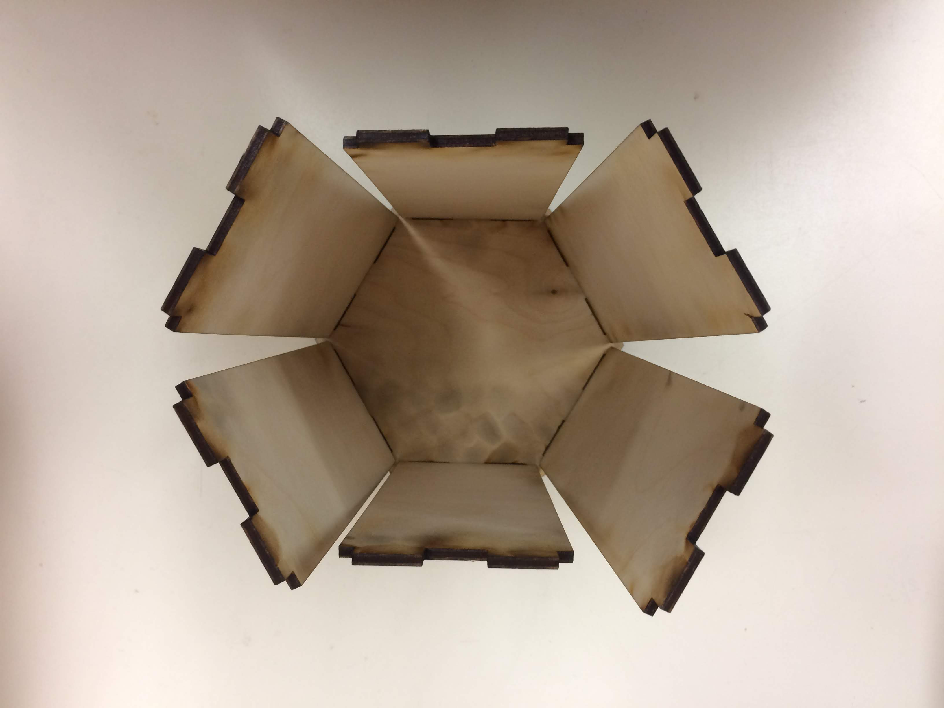
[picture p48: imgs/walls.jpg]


9. Using a mallet, and some finger dexterity, take a now dry glued obstacle base and position it so that the obstacle wall inserts are right below their corresponding holes on the obstacle base. Hammer in the base into the wall inserts as shown.

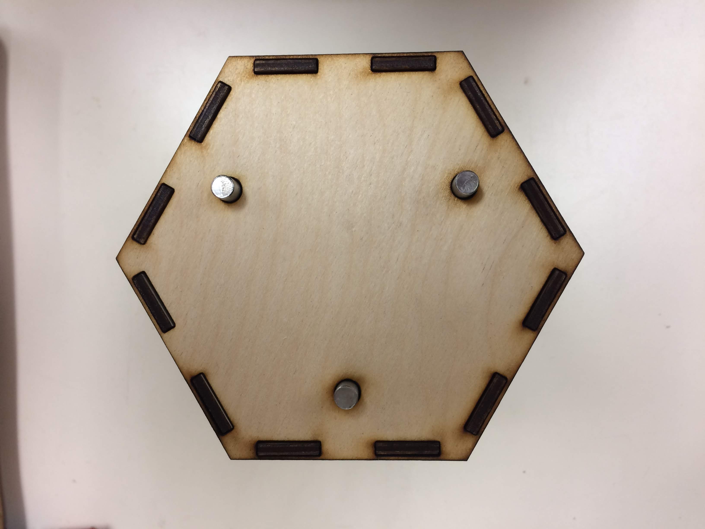
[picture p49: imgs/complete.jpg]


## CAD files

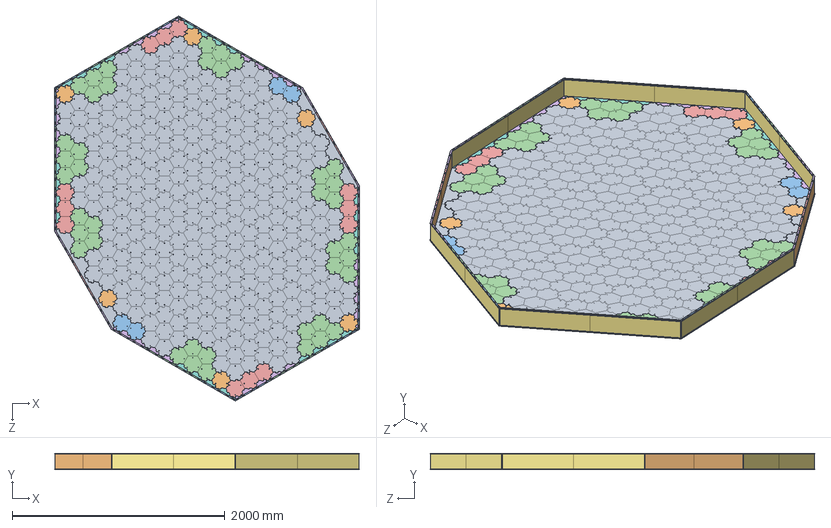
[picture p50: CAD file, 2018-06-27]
full_scale_model/modules/assemblies/full_scale.SLDASM
2870.2 x 152.4 x 3622.2 mm
module x 41
module_1cell x 6
module_2cell x 2
module_5cell x 8
module_3cell x 4
border_module x 6
Wall_seg_full x 12
border_module2 x 6
border_bigger x 4
wall_full x 4
wall_cover x 4
wall_cover_border_full x 6
wall_cover_borderbigger_full x 2
wall_border_harder x 4

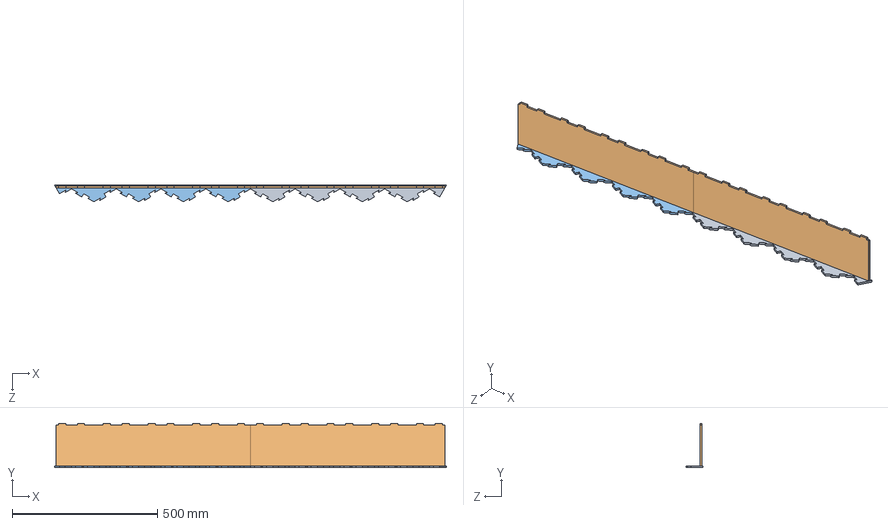
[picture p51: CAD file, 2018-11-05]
full_scale_model_mini/modules/assemblies/wall_4cell_assembly.SLDASM
1349.2 x 152.4 x 57.2 mm
border_4cell_right
wall_4cell x 2
border_4cell_left

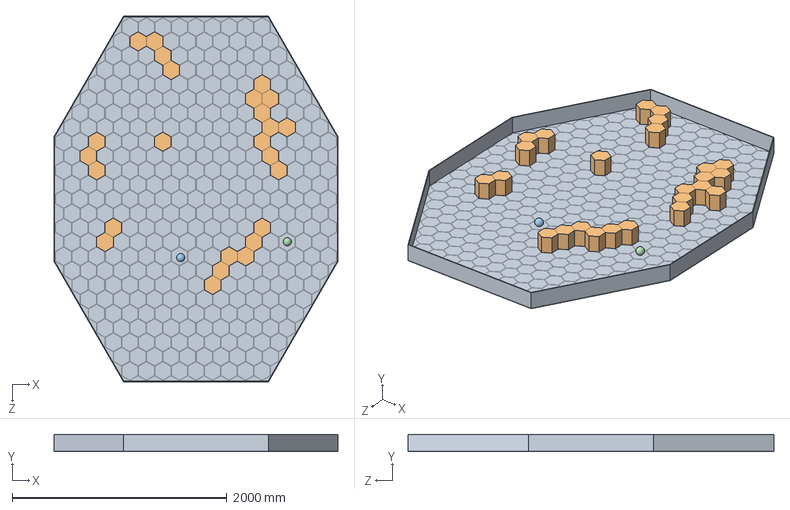
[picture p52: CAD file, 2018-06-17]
rough_full_scale_model/midentropy.SLDASM
2643.0 x 158.8 x 3403.6 mm
MazeFloor
obstacle x 25
predator
prey

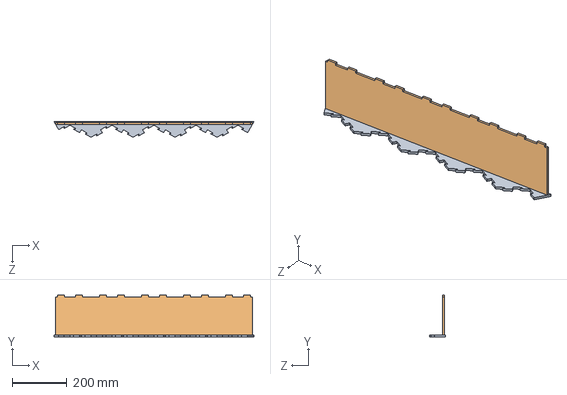
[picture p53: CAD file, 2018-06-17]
small_scale_model/modules/assemblies/Wall_seg_assembly.SLDASM
733.2 x 152.4 x 57.2 mm
border
Wall_seg

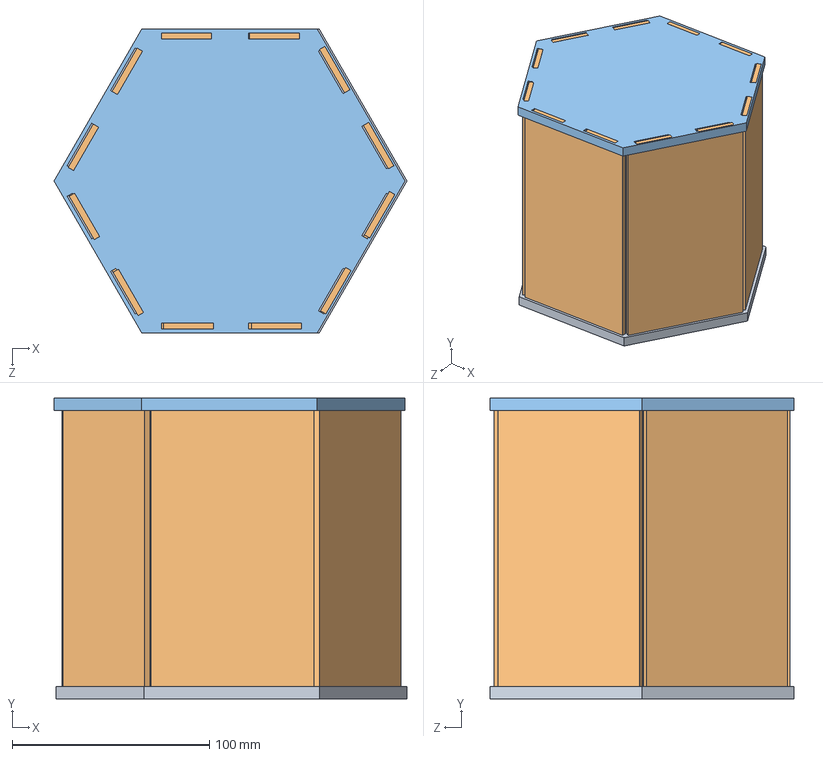
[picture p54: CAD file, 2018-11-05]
full_scale_model_mini/modules/assemblies/obstacle_assemb.SLDASM
178.8 x 152.4 x 154.0 mm
obstacle_base
obstacle_wall x 6
obstacle_cover

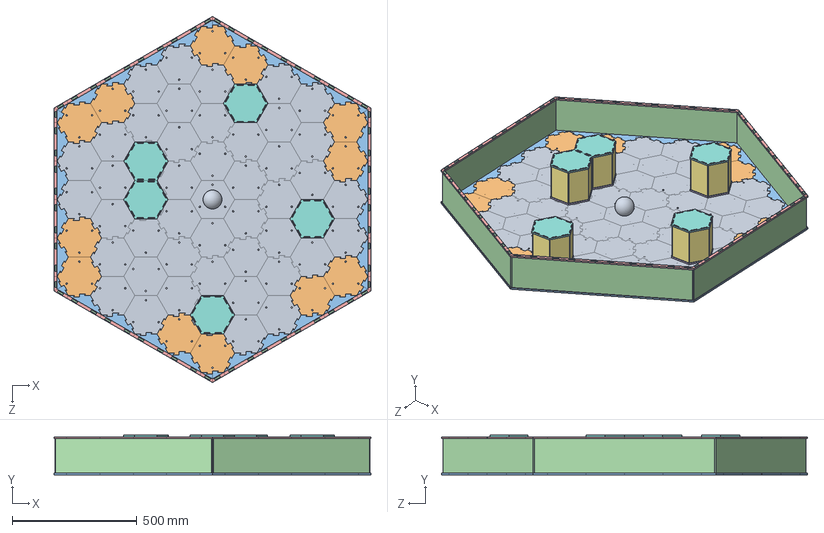
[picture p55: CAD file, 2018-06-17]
small_scale_model/modules/assemblies/maze_world.SLDASM
1270.0 x 158.8 x 1466.5 mm
module x 8
module_2cell x 6
border x 6
Wall_seg x 6
wall_cover x 6
obstacle_base x 5
obstacle wall x 30
obstacle_cover x 5
prey

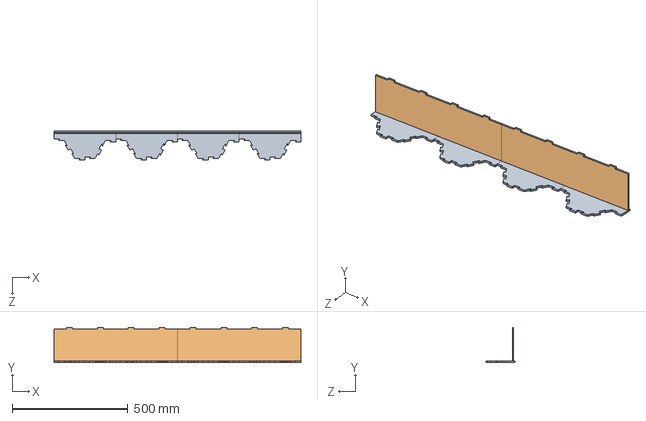
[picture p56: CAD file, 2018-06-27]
full_scale_model/modules/assemblies/wall_2cell_assembly.SLDASM
1066.8 x 152.4 x 123.7 mm
border_bigger x 2
wall_full x 2

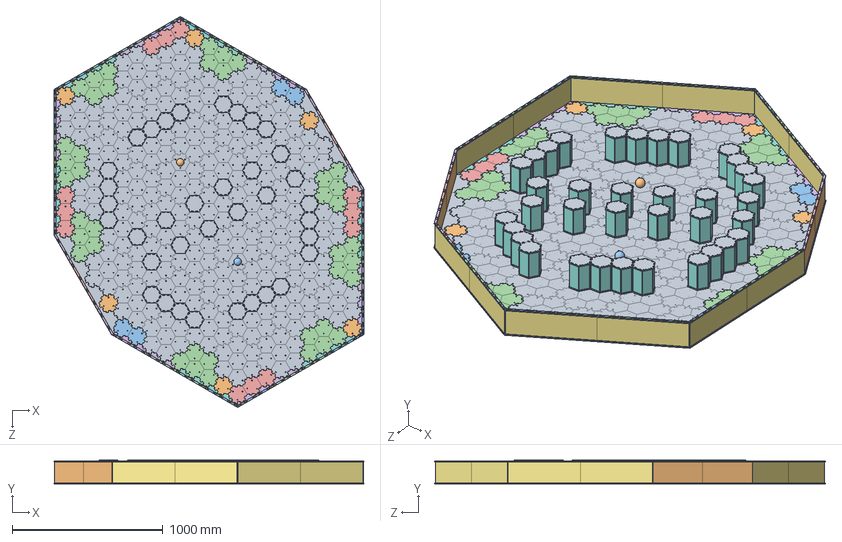
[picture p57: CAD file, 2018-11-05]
full_scale_model_mini/modules/assemblies/full_scale.SLDASM
2057.4 x 158.8 x 2595.7 mm
module_7cell x 41
module_1cell x 6
module_2cell x 2
module_5cell x 8
module_3cell x 4
border_4cell_right x 6
wall_4cell x 12
border_4cell_left x 6
border_2cell x 4
wall_2cell x 4
wall_cover x 4
wall_middle_covers_4cell x 6
wall_middle_covers_2cell x 2
wall_corner_covers_2cell x 4
obstacle_base x 36
obstacle_wall x 216
obstacle_cover x 36
prey
predator

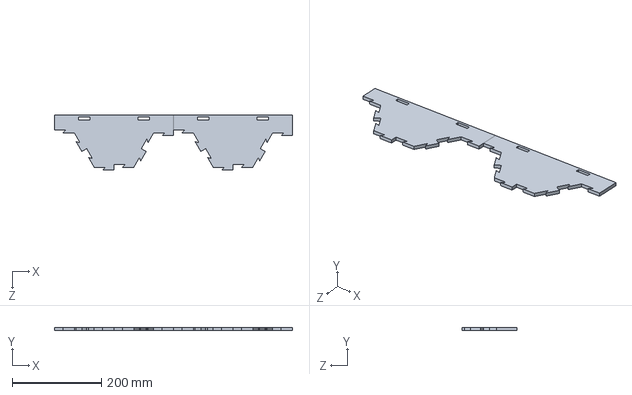
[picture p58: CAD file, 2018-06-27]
full_scale_model/modules/border_2cell/border_2cell.SLDPRT
533.4 x 6.35 x 123.7 mm

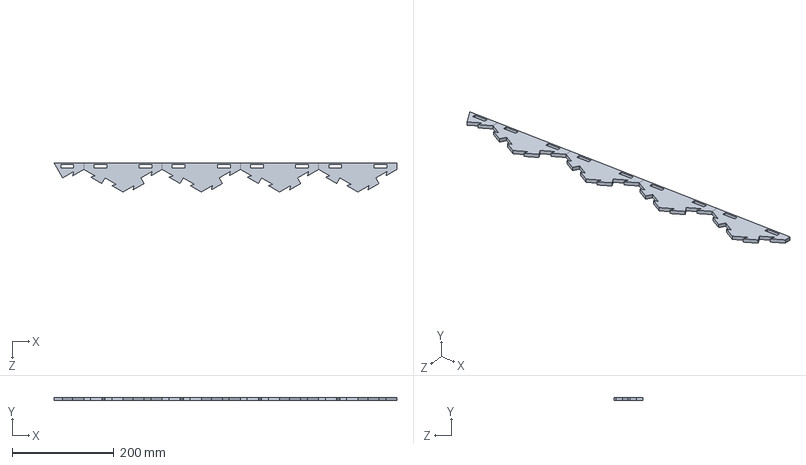
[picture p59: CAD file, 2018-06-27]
full_scale_model/modules/border_4cell_left/border_4cell_left.SLDPRT
674.6 x 6.35 x 57.2 mm

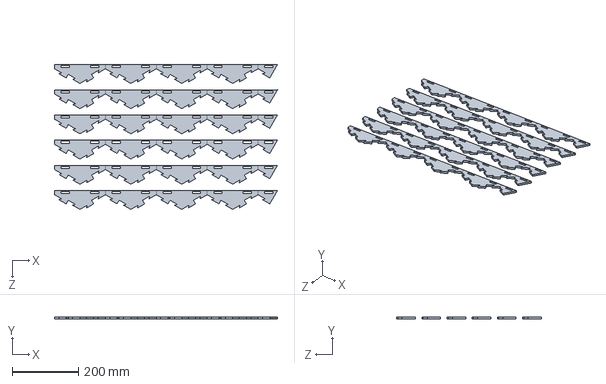
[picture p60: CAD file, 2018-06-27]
full_scale_model/modules/border_4cell_right/border_4cell_right_mult.SLDPRT
674.6 x 6.35 x 438.1 mm

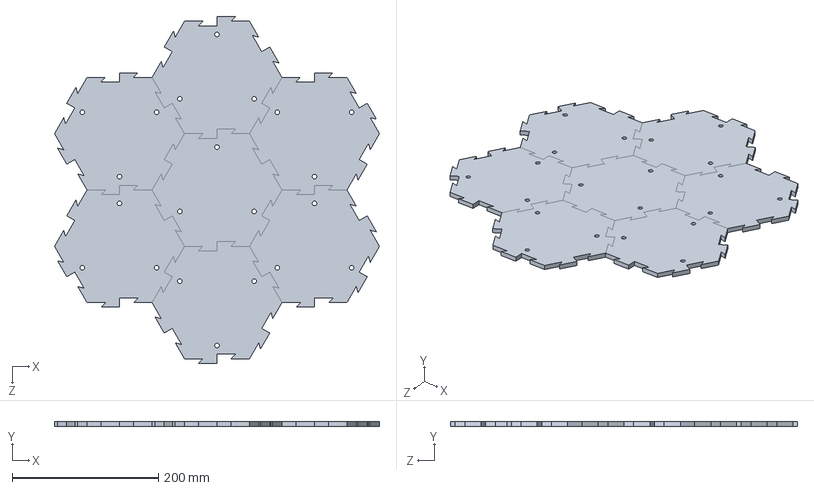
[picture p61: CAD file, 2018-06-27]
full_scale_model/modules/module_1cell/module_1cell_mult.SLDPRT
444.5 x 6.35 x 474.6 mm

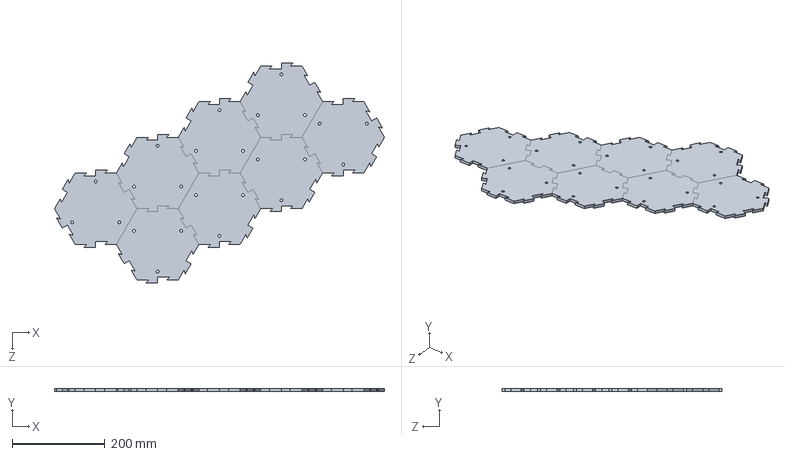
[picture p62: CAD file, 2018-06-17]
full_scale_model/modules/module_2cell/module_2cell_mult.SLDPRT
711.2 x 6.35 x 474.6 mm

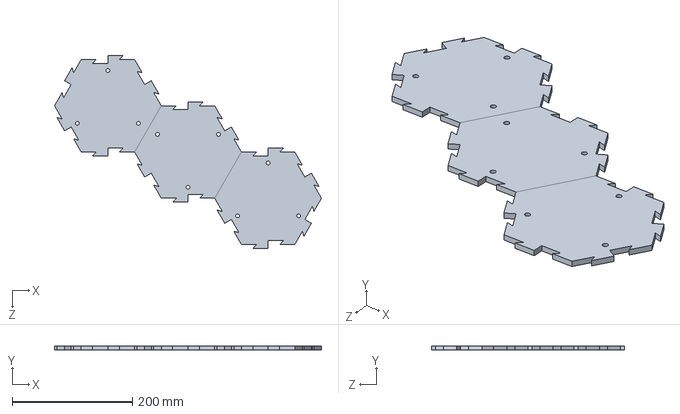
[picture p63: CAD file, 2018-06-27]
full_scale_model/modules/module_3cell/module_3cell.SLDPRT
444.5 x 6.35 x 320.7 mm

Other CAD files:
full_scale_model/modules/assemblies/wall_4cell_assembly.SLDASM
full_scale_model/modules/assemblies/obstacle_assemb.SLDASM
full_scale_model_mini/modules/assemblies/wall_2cell_assembly.SLDASM
full_scale_model/modules/module_5cell/module_5cell.SLDPRT
full_scale_model/modules/border_2cell/border_2cell_mult.SLDPRT
full_scale_model/modules/border_2cell/dxf/border_2cell_mult.DXF
full_scale_model/modules/border_4cell_left/border_4cell_left_mult.SLDPRT
full_scale_model/modules/border_4cell_left/dxf/border_4cell_left_mult.DXF
full_scale_model/modules/border_4cell_right/border_4cell_right.SLDPRT
full_scale_model/modules/border_4cell_right/dxf/border_4cell_right.DXF
full_scale_model/modules/module_1cell/dxf/module_1cell_mult.DXF
full_scale_model/modules/module_1cell/module_1cell.SLDPRT
full_scale_model/modules/module_2cell/dxf/module_2cell_mult.DXF
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

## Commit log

2018-06-17 added CAD, dxf, and svg files and images
    [Wall_seg.DXF, Wall_seg.SLDPRT, Wall_seg_assembly.SLDASM, Wall_seg_half.DXF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]
2018-06-18 changed 6cell to 7cell
    [module_7cell.DXF, module_7cell.SLDPRT]
2018-06-27 added all part files, dxf files, and svg files and rendered pics for full scale model
    [border_2cell.SLDPRT, border_2cell_mult.DXF, border_2cell_mult.SLDPRT, border_4cell_left.SLDPRT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]
2018-11-05 added mini version of the full scale model for the sphero mini robots. includes assembly, part, dxf, and svg files
    [border_2cell.SLDPRT, border_2cell_mult.DXF, border_2cell_mult.SLDPRT, border_4cell_left.SLDPRT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]
2018-11-06 updated obstacle wall design for better press fitting
    [obstacle_wall.DXF, obstacle_wall.SLDPRT, obstacle_wall_mult.DXF, obstacle_wall_mult.SLDPRT]
2018-11-07 updated hole size in obstacle base so that pins are press fit
    [obstacle_base.DXF, obstacle_base.SLDPRT, obstacle_base_mult.DXF, obstacle_base_mult.SLDPRT]
2018-12-04 added full_scale_mini laser cut pics. modified readme
